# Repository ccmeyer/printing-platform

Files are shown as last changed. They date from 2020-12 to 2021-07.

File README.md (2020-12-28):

# &#181;CD microfluidic printing system
### A system for high throughput reaction generation using sub-microliter droplet printing

<br/>

## Overview

<p align="center">
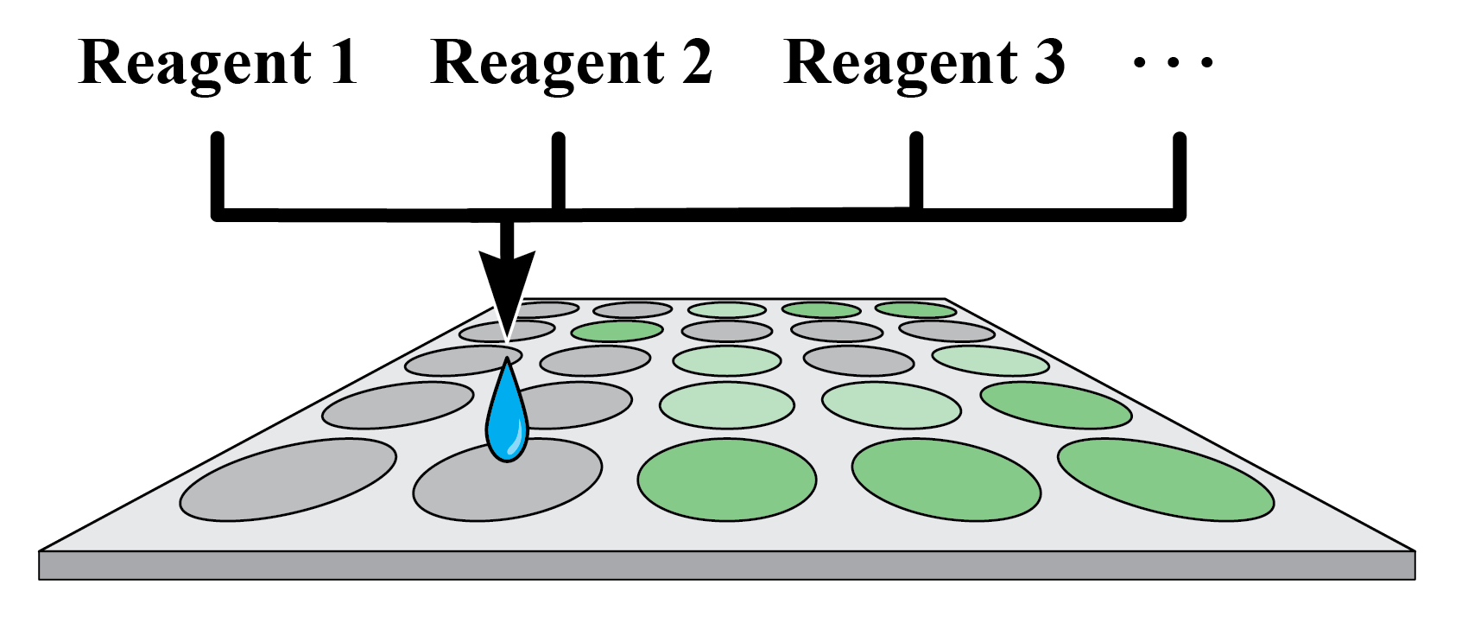
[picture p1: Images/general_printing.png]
  
</p>

The system detailed in this repository was originally described in the paper: "__________" and built upon work described in Wang, J. et al. (2019) Microfluidic cap-to-dispense (μCD): a universal microfluidic–robotic interface for automated pipette-free high-precision liquid handling. Lab Chip 19:3405-3415. This repository includes the necessary components to recreate the system shown in **Figure 1**. This repository includes the following components:
* A parts list, CAD files to 3D print or laser cut the required components, and assembly instructions [link](https://github.com/ccmeyer/printing-platform/blob/main/Documentation/assembly_description.md).

* Description of the underlying theory behind the system and how to optimize its use [link](https://github.com/ccmeyer/printing-platform/blob/main/Documentation/printing_theory_and_calibration.md).

* Description of the API required to control all components of the system [link](https://github.com/ccmeyer/printing-platform/blob/main/Documentation/API_documentation.md).

<br/>

## Printing platform

<p align="center">
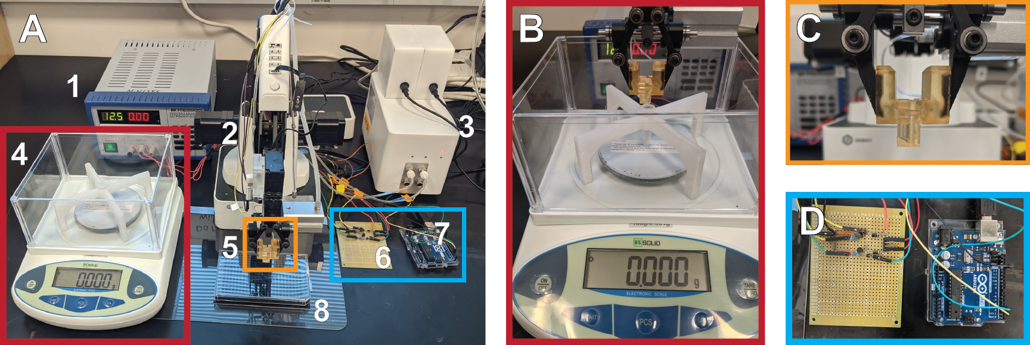
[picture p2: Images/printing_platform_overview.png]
uCD printing system
  
</p>

<p align="center">
  <strong>Figure 1</strong> Diagram of the complete printing platform. (A) Image of the full platform, 1) 12.5V DC power supply, <br>2) Dobot robotic arm, 3) Precigenome pressure regulator, 4) Analytical balance, 5) Gripper holding a printer head, <br>6) Valve control circuit, 7) Arduino Uno microcontroller, 8) Well plate. (B) Close up of the printer head positioned <br>over the reagent tube during calibration. (C) Dobot gripper with the 3D printed gripper adapters holding <br>a printer head. (D) Valve control circuit connected to an Arduino
</p>

The core of the μCD system is a disposable multilayer microfluidic container composed of a 3D printed reservoir linked to a microfluidic printing nozzle with two pneumatic control channels that can be reversibly connected to a robotic arm. This robotic arm is customized to enable reliable linking between the pneumatic controllers and the microfluidic device. The modular and disposable design of the μCD system allows for the inclusion of limitless reagents in a multicomponent experiment as the microfluidic devices are can be swapped in and out without risk of cross-contamination.

The printing platform is comprised of several critical components:
* The three-dimensional positioning and loading of printer heads are achieved using the Dobot magician robotic arm with the gripper attachments. 
* The printing and refuel pressures are regulated by the Precigenome pressure regulator. 
* The Arduino and valves are used to apply the pressures in bursts for printing and refueling.
* The storage and printing is carried out in the disposable microfluidic printing heads.

A detailed description of the components and assembly can be found [here](https://github.com/ccmeyer/printing-platform/blob/main/Documentation/assembly_description.md).

<br/>

## Printing concept

<p align="center">
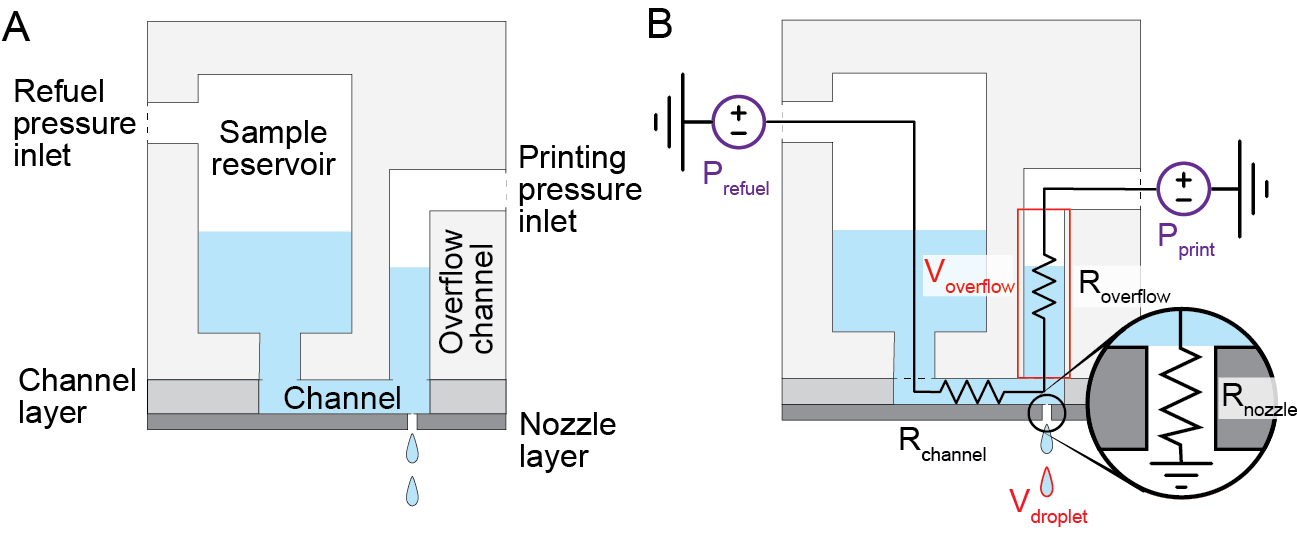
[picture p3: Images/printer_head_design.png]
Printer head design
  
</p>

<p align="center">
  <strong>Figure 2</strong> Schematic depicting the printer head design. A) Labels the components of the printer head. B) Overlay of <br>the parameters of the system. Tunable parameters: purple, fixed parameters: red, unknown parameters: black.
</p>

The system is built upon the concept of microfluidic adaptive printing. The core principle is to apply bursts of force to liquid, squeezing it through a small ejection port (<100 &#181;m) which causes it to pinch off as a nanoliter scale droplet. In our instantiation of this system we use air pressure to exert the force and a small nozzle fabricated out of PMMA to serve as the exit port. The primary variables governing the activity of the system are highlighted in **Figure 2** and are explained in detail [here](https://github.com/ccmeyer/printing-platform/blob/main/Documentation/printing_theory_and_calibration.md).

<br/>

## Platform API

The bulk of the API is included under the umbrella of the `Platform` class. This class includes the functions to intitially connect to and control all of the components that comprise the system. The general tasks that are routinely needed have been divided to make the customization of new protocols accessible. Several manual drive modes have been included to allow for the control of the system from the keyboard. This allows for the quick adaption of processes by the user to prototype protocols or run full experiments. 

The other class is the `PrinterHead` class which is used to track individual printer heads. This makes the tracking of volumes of the reagent are required parameters that are unique to each printer head and reagent to be tracked easily. 

The major steps required to utilize the code is detailed [here](https://github.com/ccmeyer/printing-platform/blob/main/Documentation/API_documentation.md).

<br/>

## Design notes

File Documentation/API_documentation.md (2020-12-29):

# Printing platform API documentation

## `Platform` class

* This is a class used to store the necessary variables required to operate the platform as well as handle all communication with the Dobot, Arduino and pressure regulator

### Dobot communication

`init_dobot()`
* Establishes the connection to the Dobot.
* Sets its movement parameters.
* Reads in the print calibration file which includes the locations of the loading and tube positions.
* Activates the gripper.

`get_plate_data()`
* Reads in the desired file path of the JSON file describing the plate information
* The information includes the well spacing, number of rows and columns and the positions of the four corner wells of the plate
* Generates a transformation matrix to get the corrected well XY-coordinates to ensure accurate Dobot positioning
* Finds the change in Z coordinates moving down the rows or across the columns and assumes a linear change in value to correct the Z coordinate for each well
* To create a new plate use the provided template in the 'Calibrations' directory
* Coordinates are stored as a dictionary with the three keys 'x', 'y', and 'z'

`write_plate_data()`
* Takes all of the current plate data and updates the metadata file that was originally loaded

`gen_trans_matrix()`
* Takes the location of the four corner wells and the plate dimensions and applies the `getPerspectiveTransform()` function from the OpenCV library to perform a four point transformation to map the actual location of the four wells to the expected location
* Then takes the inverse of the matrix so that it can be used to transform the expected coordinates of a well to the actual coordinates

`get_well_coords()`
* Take the desired row and column index and returns the corrected coordinates for the target well
* Uses the transformation matrix to take the expected coordinates and transform them into the real coordinates

`home_dobot()`
* First resets the Dobot's position to avoid having the arm hit the surrounding components during the homing process
* Runs the Dobot homing command
* Sets the location to the 'home' state
* This function should be called before performing any movements with the Dobot to ensure that it has its position correct

`move_dobot()`
* Takes XYZ coordinates and moves the Dobot to those coordinates

`dobot_manual_drive()`
* Drops into a manual drive mode controlled from the keyboard
* X direction is controlled using 'w' and 's'
* Y direction is controlled using 'a' and 'd'
* Z direction is controlled using 'k' and 'm'
* The step or amount that is moved is set using the 'f' to increase the step size and 'v' to decrease it. The step values are in mm
* To quit the manual drive mode, press 'q'

`change_print_position()`
* Initiates a protocol to modify the expected well locations of a given plate
* Moves from corner to corner and drops into `dobot_manual_drive()`to allow the operator to manually drive the Dobot to the correct location of each well to compensate for any deviations
* Once all the points are corrected, the new positions are stored in the plate metadata file.
* It is recommended to run this protocol prior to running any experiments to make sure that the positions are perfect
* Not that necessary for 96-well plates but should always be performed for 384-well plates
* The actual calibration protocol is described in detail [here]

`change_tube_position()`
* Moves to the currently saved tube position used during the printer head calibration protocol
* Drops into the `dobot_manual_drive()` mode to manual correct the position

`move_to_tube_position()`
* Moves to the currently saved tube position used during the printer head calibration protocol
* First moves above the tube to ensure that the arm does not hit the tube as it is located above the plate and the dobot uses point to point movement

`move_to_loading_position()`
* Moves to the currently saved loading position used during the printer head calibration protocol
* Used when switching out printer heads

`move_to_well(row,column)`
* Takes the desired row and column indexes and input and moves to the correct coordinates
* Checks to make sure that the target well is present in the plate

`load_gripper()`
* Initiates a protocol to open and close the gripper to make exchanging printer heads easier.

`disconnect_dobot()`
* Deactivates the gripper
* Disconnects from the Dobot

<br>

### Arduino communication

`init_ard()`
* Takes in the COM port of the Arduino and opens up serial communication
* Currently set to 'COM6' and would need to be changed to the correct COM port if that is incorrect

`print_droplets()`
* Takes the desired frequency, pulse width, refuel width, and droplet count for a printing command
* Serializes all the values and passes it to the Arduino and then pauses briefly
* Sends a second signal to the Arduino to confirm the end of transmission
* Waits to receive a signal from the Arduino that the printing protocol has been completed

`refuel_test()`
* Defined printing protocol used in calibration of the refuel process

`pulse_test()`
* Defined printing protocol used in calibration of the printing step

`refuel_open()`
* Opens the refuel valve and leaves it open

`pulse_open()`
* Opens the printing valve and leaves it open  

`close_valves()`
* Closes both valves

`close_ard()`
* Closes communication with the Arduino

<br>

### Pressure regulator communication

`init_pressure()`
* Initiates the Precigenome pressure regulator and the two channels used for refueling and printing

`set_pressure()`
* Takes in pressure values for the refuel and printing channels

`pressure_on()`
* Turns both pressure channels on

`pressure_off()`
* Turns both pressure channels off

`pressure_test()`
* Used to verify that the complete system is air tight
* Applies high pressure and records the flow
* If the flow rate is high that means that there is a leak in the system that needs to be addressed
* Load the gripper with position calibration chip so that the outlets that connect with the printer heads are seal to ensure proper seal
* The pressure test protocol is described in more detail [here]

`close_reg()`
* Closes communication with the pressure regulator

<br>

### Full platform functions

`initiate_all()`
* Opens communication with all three components

`drive_platform()`
* Comprehensive manually driving function
* Within this method, the operator is able to move the dobot by wells, load and unload the gripper, set and control pressures, and print defined arrays
* The exact functions executed by the drive function can be found in the print_platform_API.py file
* The key assignments can be easily changed to customize the use of drive function

`resistance_testing()`
* Initiates the printer head calibration protocol
* Creates a `PrinterHead` object and asks for the channel volume of the printer being used and then density of the reagent
* Sets the target droplet volume to 60 nL
* Monitors the refuel and printing steps and calculates the resistance of each component of the printer head
* A detailed description of this process can be found [here]

`print_array()`
* Takes a CSV file in the Print_arrays directory and prints the specified number of droplets into the target wells
* A template CSV file can be found in the Print_arrays directory

`disconnect_all()`
* Closes all communication with all three components

<br>

## `PrinterHead` class

* This is a class that is used to store all of the information associated with each printer head required for accurate printing with each printer head.
* Includes specifics about the reagent including its name and density and the printer head such as its overflow channel volume.
* It also contains all of the calibration information including the calculated resistances and the required pressures to print the desired droplet volume. 

<br>

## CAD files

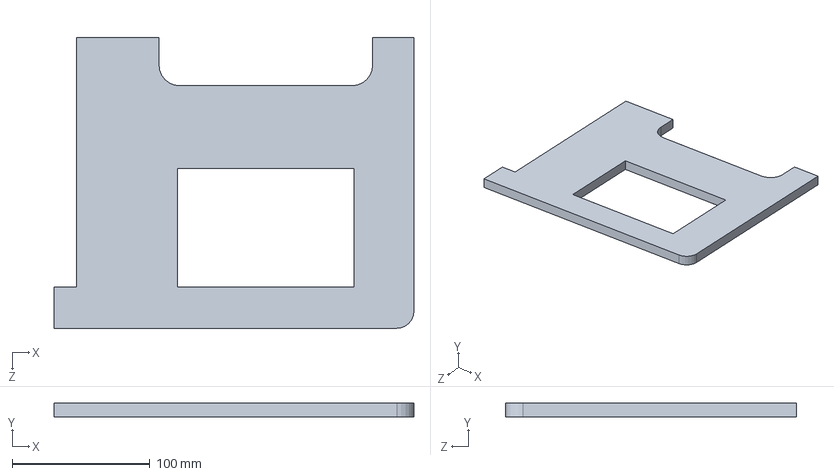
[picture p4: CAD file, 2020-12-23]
CAD_files/arm-plate_holder_template.SLDPRT
261.2 x 10.0 x 210.9 mm

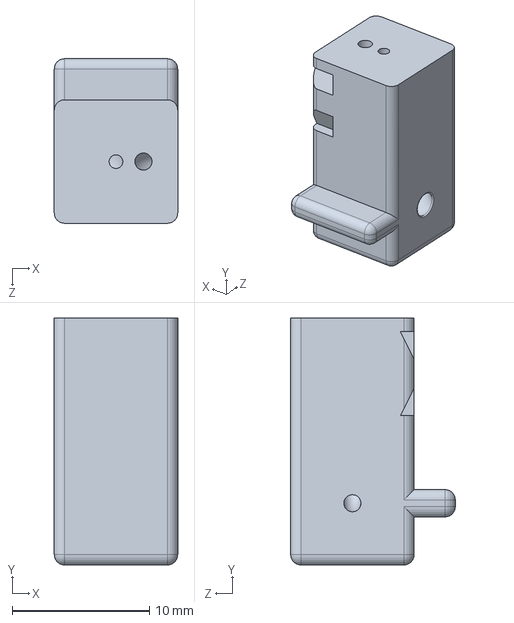
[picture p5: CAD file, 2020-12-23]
CAD_files/printer_head.SLDPRT
9.00 x 18.0 x 12.0 mm

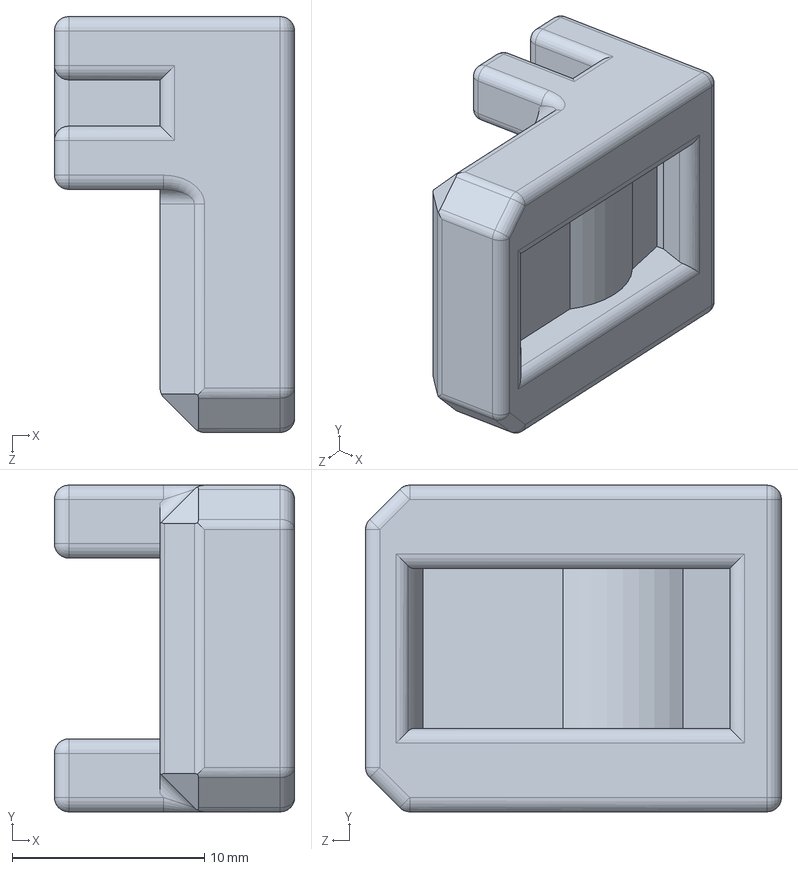
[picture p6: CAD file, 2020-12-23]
CAD_files/gripper_adapter_refuel_side.SLDPRT
12.5 x 17.0 x 21.6 mm

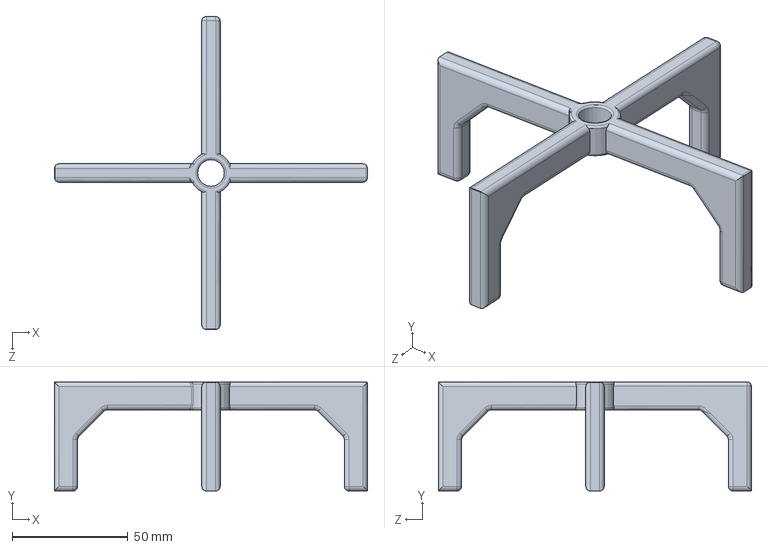
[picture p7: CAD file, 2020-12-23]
CAD_files/balance_tube_holder.SLDPRT
135.0 x 47.0 x 135.0 mm

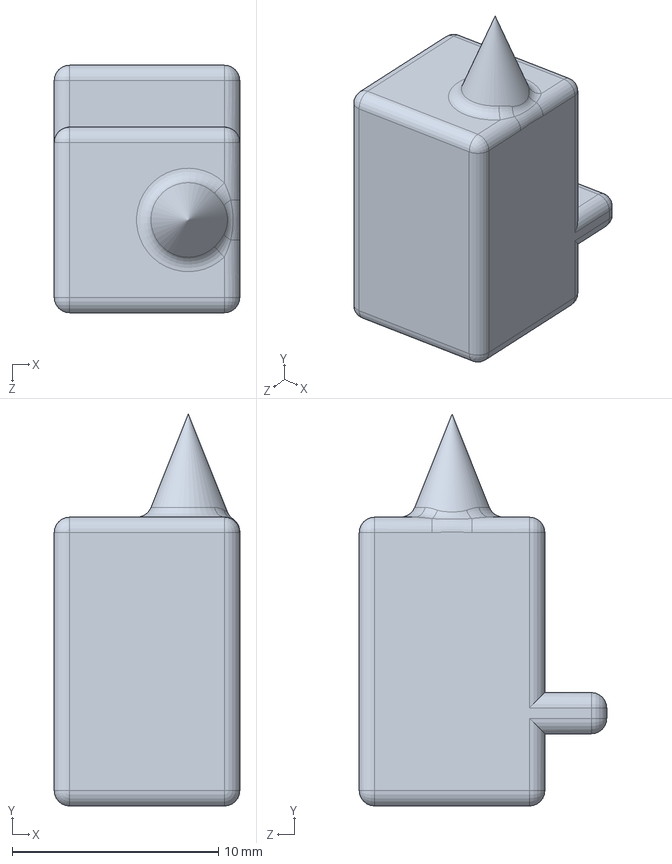
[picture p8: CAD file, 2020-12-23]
CAD_files/position_calibration_chip.SLDPRT
9.00 x 19.0 x 12.0 mm

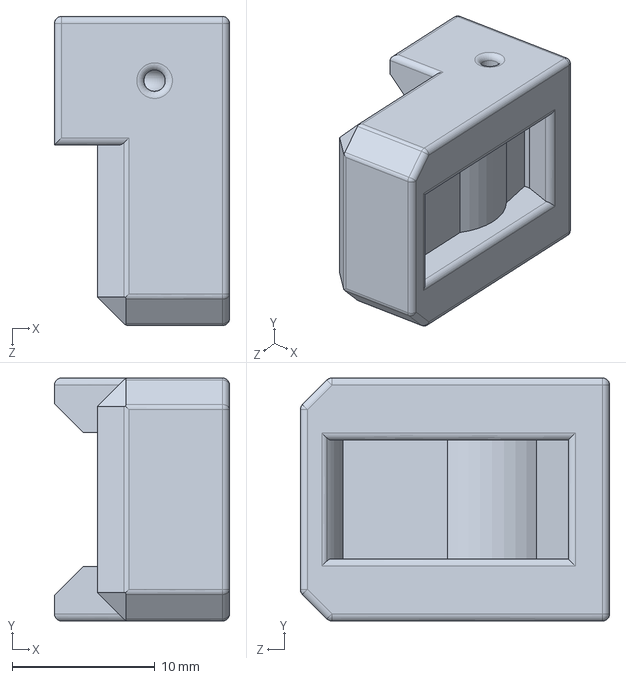
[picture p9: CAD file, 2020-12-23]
CAD_files/gripper_adapter_print_side.SLDPRT
12.2 x 17.0 x 21.6 mm

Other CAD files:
CAD_files/balance_tube_holder.STL
CAD_files/gripper_adapter_print_side.STL
CAD_files/gripper_adapter_refuel_side.STL
CAD_files/position_calibration_chip.STL
CAD_files/printer_head.STL

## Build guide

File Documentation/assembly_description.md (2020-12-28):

# Printing platform assembly

<p align="center">
  µCD printing system
</p>

<p align="center">
  <strong>Figure 1</strong> Diagram of the complete printing platform. (A) Image of the full platform, 1) 12.5V DC power supply, <br>2) Dobot robotic arm, 3) Precigenome pressure regulator, 4) Analytical balance, 5) Gripper holding a printer head, <br>6) Valve control circuit, 7) Arduino Uno microcontroller, 8) Well plate. (B) Close up of the printer head positioned <br>over the reagent tube during calibration. (C) Dobot gripper with the 3D printed gripper adapters holding <br>a printer head. (D) Valve control circuit connected to an Arduino
</p>

The printing platform is comprised of several different components. The three-dimensional positioning and loading of printer heads are achieved using the Dobot magician robotic arm with the gripper attachments. The printing and refuel pressures are regulated by the Precigenome pressure regulator. The Arduino and valves are used to apply the pressures in bursts for printing and refueling. The assembled system is shown in **Figure 1**. 

## Material list

1.	PMMA sheets (75 μm thick)
2.	Double-sided adhesive membrane (ARcare 90445, Adhesives Research, 80 μm thick)
3.	CO2 laser cutter (Universal Laser Systems, VersaLaser 2.30)
4.	85 μm nozzle in 75 μm thick PMMA (Jestar Mold Tech Co., Ltd)
5.	SLA 3D printer (Form 3 Formlabs)
6.	Clear Resin (Formlabs)
7.	Analytical Balance (U.S Solid 1mg or ideally 0.1mg precision)
8.	Robotic arm (Dobot Magician)
9.	Two mini solenoid valves (LHDA1221111H, Lee Co)
10.	Manifold (Lee Co.)
11.	Automated pressure regulator (Precigenome Pressure/Flow controller light version, PG-MFC-LT2CH-X)
12.	Microcontroller (Arduino Uno)
13.	12.5V Power supply (BK precision programmable DC power supply)
14.	Thin tubing (1/16” and 1/8” Tygon® S3™ E-3603 Non-DEHP Laboratory Tubing)
15	Diode 1N4005
16.	Zener Diode 1N4757 51V
17.	Transistor MJH11022G
18.	Resistor 330 Ω
19.	Connector wires
20.	Breadboard

## Steps to assembe the platform

1. Connect the gripper attachment to the Dobot 

2. 3D print the two different gripper adapters for both the refuel and printing side. Attach the gripper adapters, shown in **Figure 2**, to the end effector.

<p align="center">
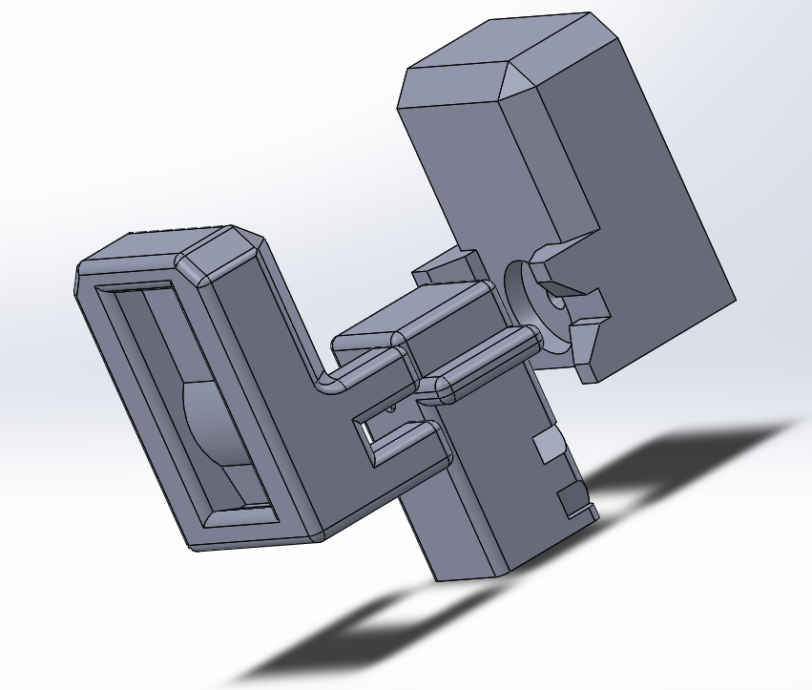
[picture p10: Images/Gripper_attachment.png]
Gripper attachments
  
</p>

<p align="center">
  <strong>Figure 2</strong> Gripper adapters used to accurately grip the printer heads
</p>

2. Screw each valve into the manifold and attach it to Dobot near the gripper (see Note 11).

3. Connect the gripper adapters to the manifolds using the thin tubing. Then connect the manifolds to the corresponding pressure outlets on the Precigenome pressure regulator.

4. Construct the circuit shown in **Figure 3** and connect the Arduino, the two valves and the power source to it Provide enough extra tubing and wires to run them along the arm to not restrict its motion while in use.

<p align="center">
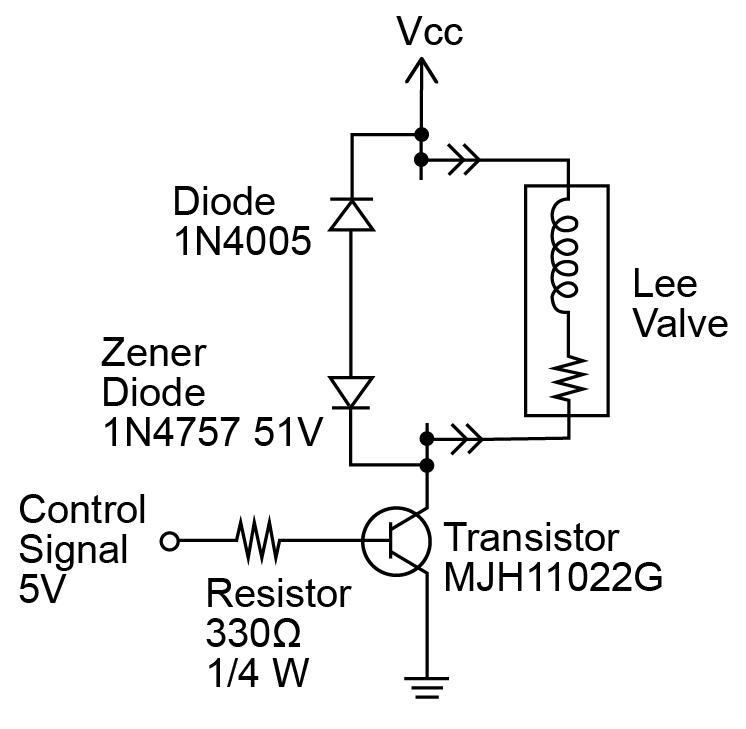
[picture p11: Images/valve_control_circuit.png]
Valve control circuit
  
</p>

<p align="center">
  <strong>Figure 3</strong> Circuit design used to regulate the valves controlling the pressure flow using the Arduino
</p>

5.	Set the voltage of the power source to 12.0 V or the required voltage for the valves.

6.	Laser cut the provided [template] and place around the Dobot to provide consistent placement of the well plate and balance in the Dobot’s Cartesian coordinate system.

7.	Connect the arm, the pressure regulator, and the Arduino to your computer.

8.	Upload the provided Arduino program to the Arduino provided [here].

9.	3D print the tube stand and place on top of the scale.

## Steps to assemble the printer heads

1.	To fabricate the layer with the small nozzle, a UV-laser is used to ablate a small hole (65-85µm diameter) into a PMMA sheet. A range of nozzle diameters can be used to give different size droplets. The nozzles can be fabricated by the following companies: Jestar Mold Tech Co., Ltd (China) and Micron Laser Technology Inc. (USA).

2.	The channel layer can be fabricated using a CO2 laser to ablate microchannels in double-sided membrane adhesive. The chosen channel width was 200 μm.	A wide range of channel widths and lengths can be used. Choose the width based on the desired channel resistance. 

3.	The bulk component of the printer head, which contains the connections to the pressure inlets and the reagent reservoir, is fabricated by 3D printing. We used stereolithography (SLA) printing with surgical guide photosensitive resin to generate the printer heads and the gripper adapters. It is critical that these printer heads are watertight, transparent and have smooth channels for proper use. These qualities are very difficult to achieve with standard fused deposition modeling (FDM) printers as there are many imperfections at the junctions between layers.

4.	The full printer head is assembled stepwise:

5.	Peel one side from the adhesive layer containing the channel and adhere it to the bottom of the 3D printed component. Line up the entry and exit holes of the channel with the corresponding openings on the 3D printed part.

6.  Peel off the other side of the adhesive layer and place the nozzle layer on top. Ensure that the small nozzle is lined up with the exit of the channel. Firmly press the layers down to make sure that there are no air pockets.

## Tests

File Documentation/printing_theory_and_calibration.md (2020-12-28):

# Printing theory

<p align="center">
  Printer head design
</p>

<p align="center">
  <strong>Figure 1</strong> Schematic depicting the printer head design. A) Labels the components of the printer head. B) Overlay of the parameters of the system. Tunable parameters: purple, fixed parameters: red, unknown parameters: black.
</p>

The complicated underlying fluid dynamics of the droplet printing system can be modeled using a simple fluid flow equation relating pressure, flow, and resistance.

<p align="center">
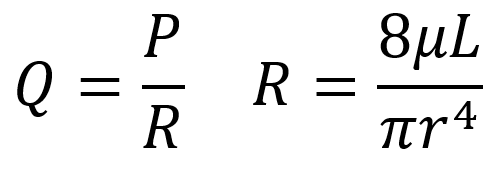
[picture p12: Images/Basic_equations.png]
Basic equations
  
</p>

In the above equations Q is flow, P is pressure, R is resistance, &#181; is viscoity, L is length, and r is the radius of the channel. At the scale of this system the interfacial tension and surface roughness and other unknown factors cause the resistance to not follow this idealized description. However, this equation helps depict the variables that the resistance, and therefore flow, depends on. Specifically the viscosity of the reagent and the radius of the nozzle. The major variables of this system are shown in **Figure 1** using the same notation as above.

While in an ideal world the properties of all reagents would be the same and the fabrication would be perfect, in reality these are often not true. The viscosity of different reagents can vary starkly such as comparing cell lysate to water. The fabrication, especially of the small nozzle, often varies and when the resistance of the nozzle is dependent on the radius of the hole to the fourth power small imperfections lead to deviations from the expected droplet volume. 

To address this issue, a calibration method has been developed to rapidly account for the differences in the printer head and the reagent simultaneouslly to achieve nanoliter resolution.

<br>

# Calibration theory

The fundamental idea of this calibration process is to leverage the fixed and tunable parameters to both determine and then account for the unknown parameters. The parameters of the system are: Unknown - Channel and nozzle resistances; Fixed - Overflow chamber volume; Tunable - Refuel and printing pressures. The primary objective of this process is to determine the printing pressure needed to eject the desired droplet volume and the refueling pressure to replenish the overflow chamber for continuous printing.

The pressures can be determined using a simple stepwise procedure beginning by calculating the unknown channel, total, and nozzle resistances

### Refuel resistance

<p align="center">
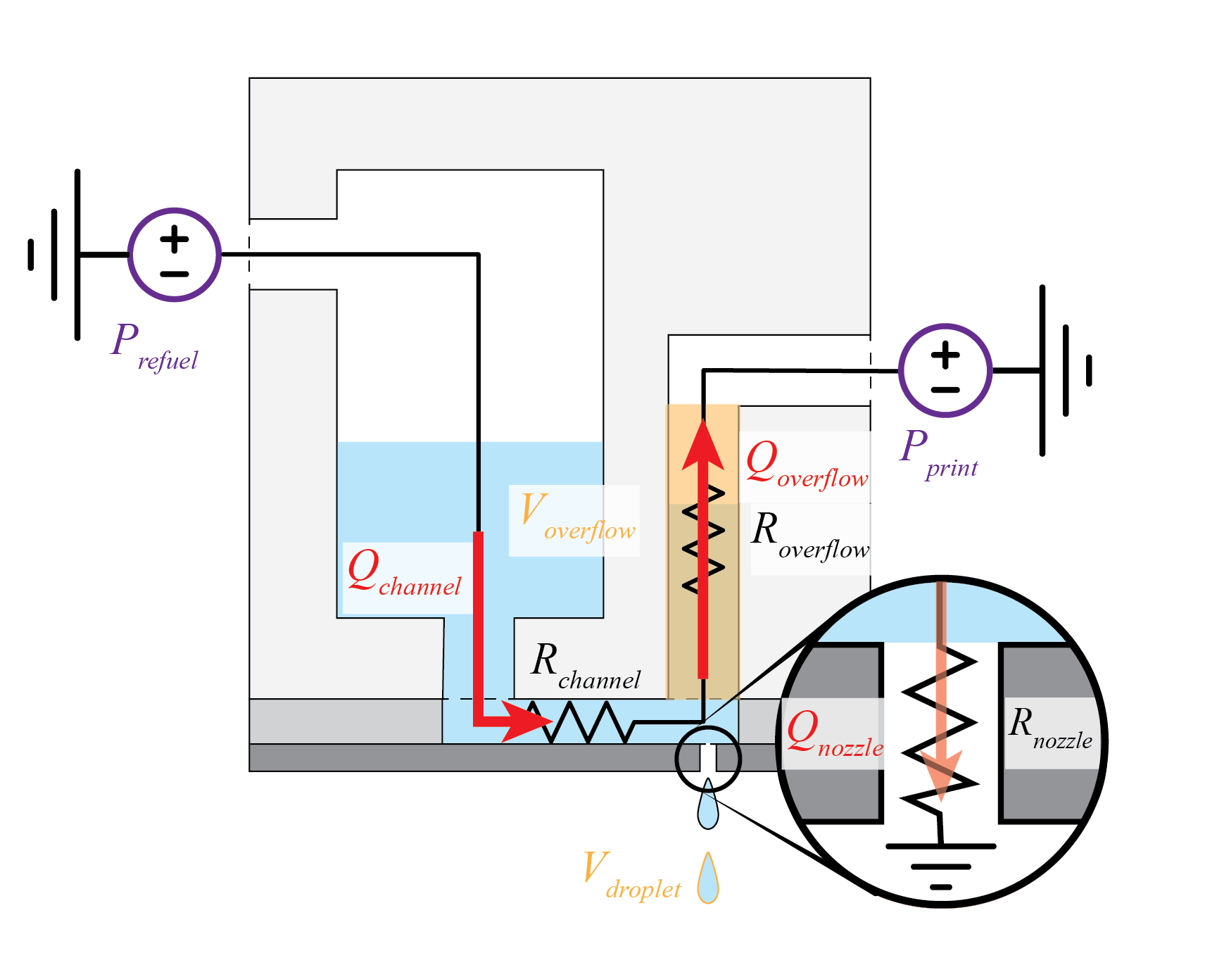
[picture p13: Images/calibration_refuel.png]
Refuel
  
</p>

<p align="center">
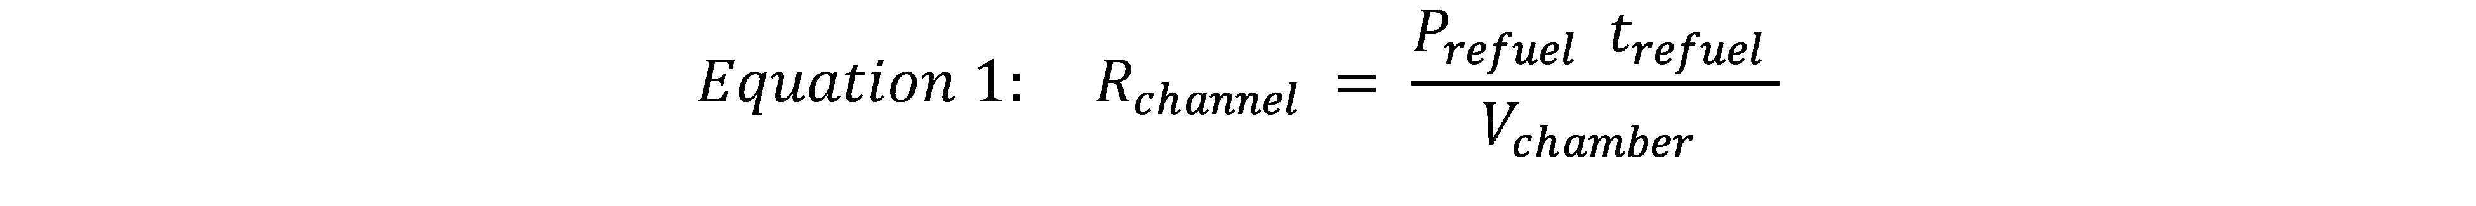
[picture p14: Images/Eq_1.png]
Equation 1
  
</p>

By applying small bursts of refuel pressure, the time required to fill the volume of the overflow channel using a set pressure can be determined. Plugging these values into Equation 1 gives the resistance of the channel. 

<br>

### Total printing resistance

<p align="center">
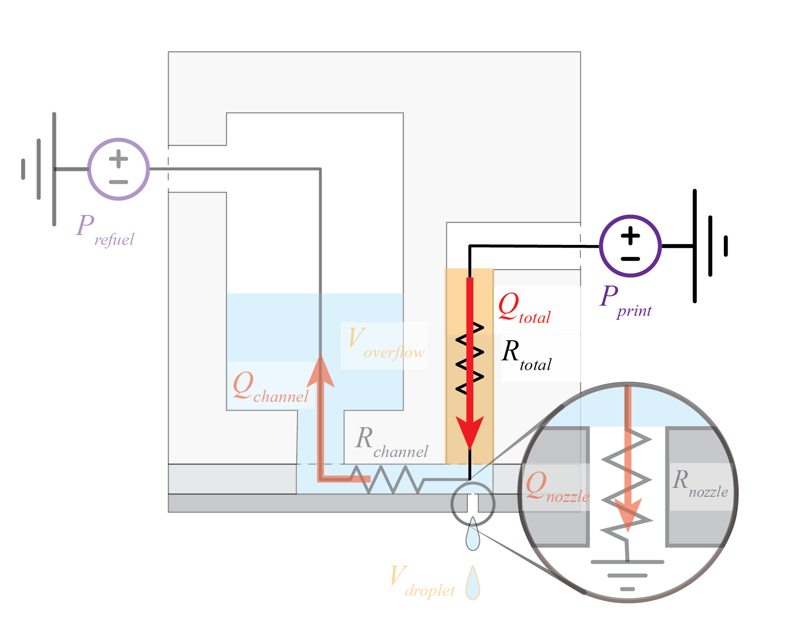
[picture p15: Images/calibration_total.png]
Total
  
</p>

<p align="center">
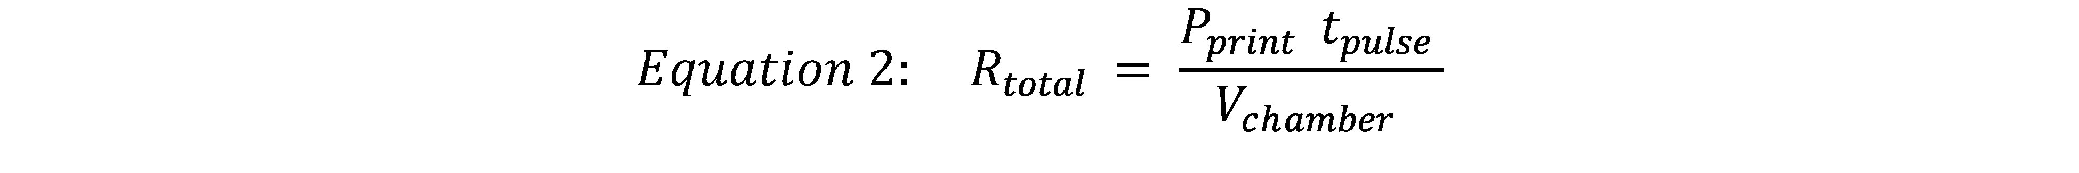
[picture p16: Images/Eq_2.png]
Equation 2
  
</p>

The total printing resistance is calculated using the same process as was used to find the refuel resistance except that now the printing pressure is applied in bursts and the time required to empty the overflow channel is monitored. Using Equation 2 allows for the calculation of the total printing resistance. This resistance does not represent the resistance of the nozzle as the flow out of the overflow channel is split between flowing through the nozzle and back through the channel. This value is necessary to know for later tuning the refuel pressure. By changing the channel length and width will change the resistance of the channel which will modulate how much back flow there is.

<br>

### Nozzle resistance
<p align="center">
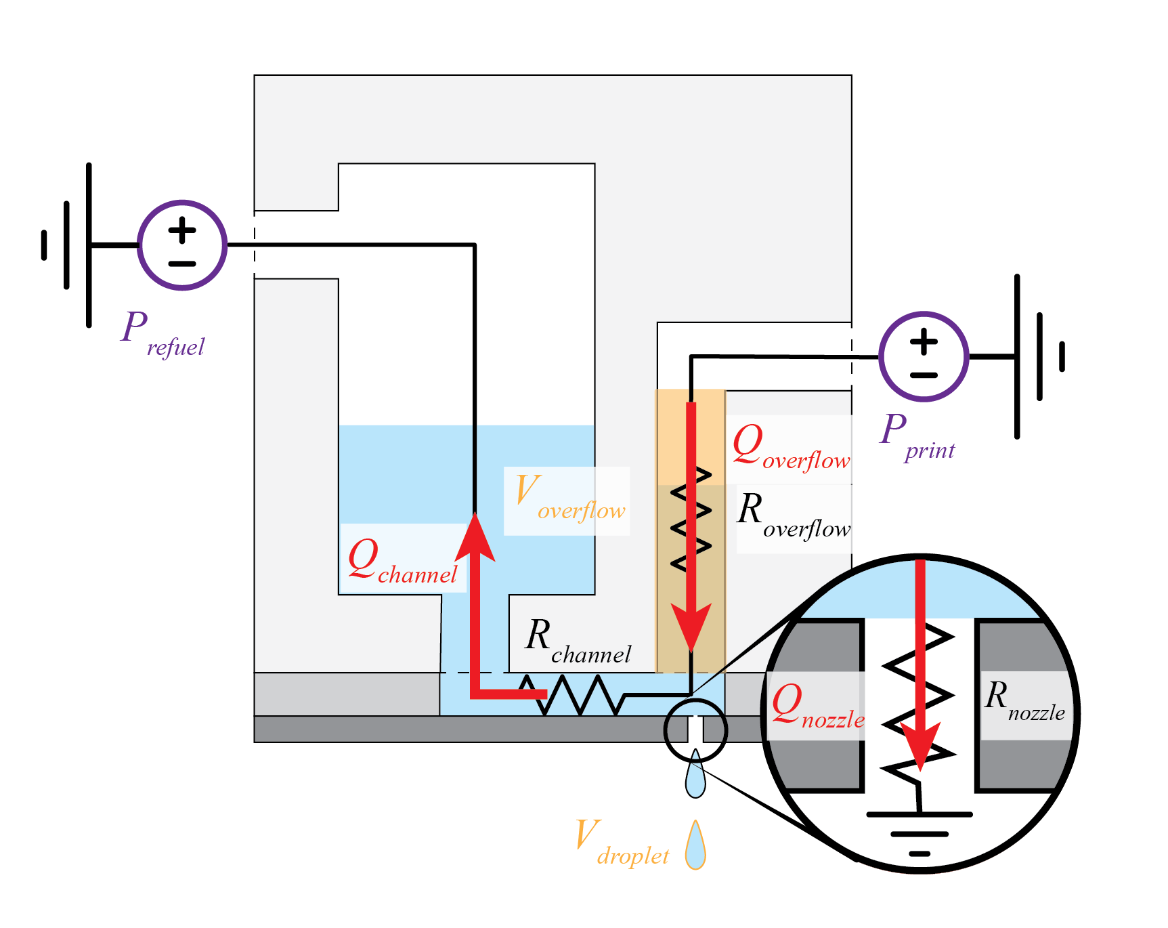
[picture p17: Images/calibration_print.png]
Print
  
</p>

<p align="center">
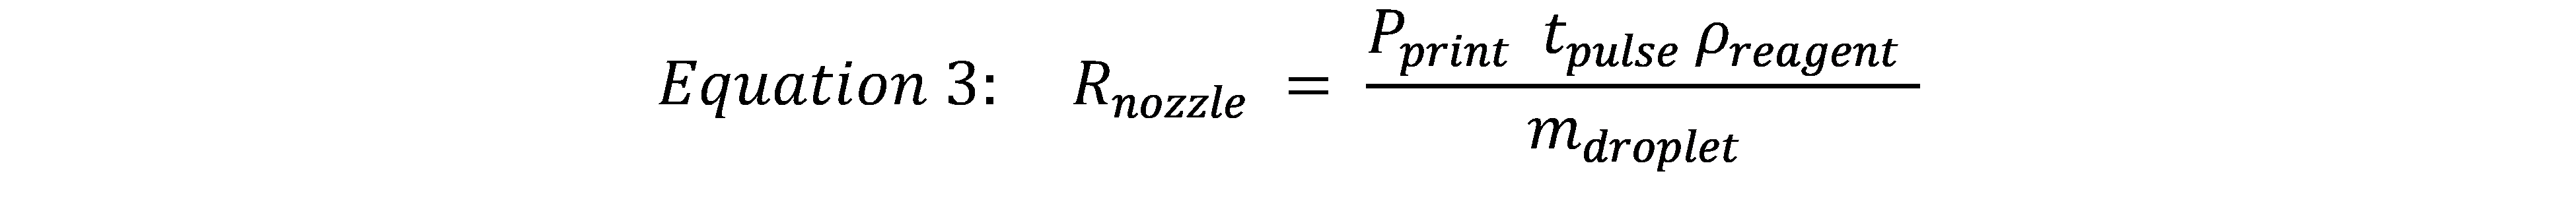
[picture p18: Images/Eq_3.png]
Equation 3
  
</p>

Through the process of calculating the total resistance, the ejected droplets are collected and used to calculate the volume of liquid that was displaced during the printing bursts. Using this volume and the known pressure and time of its application, the flow through the nozzle and its resistance can be calculated using Equation 3.

<br>

### Printing pressure 

<p align="center">
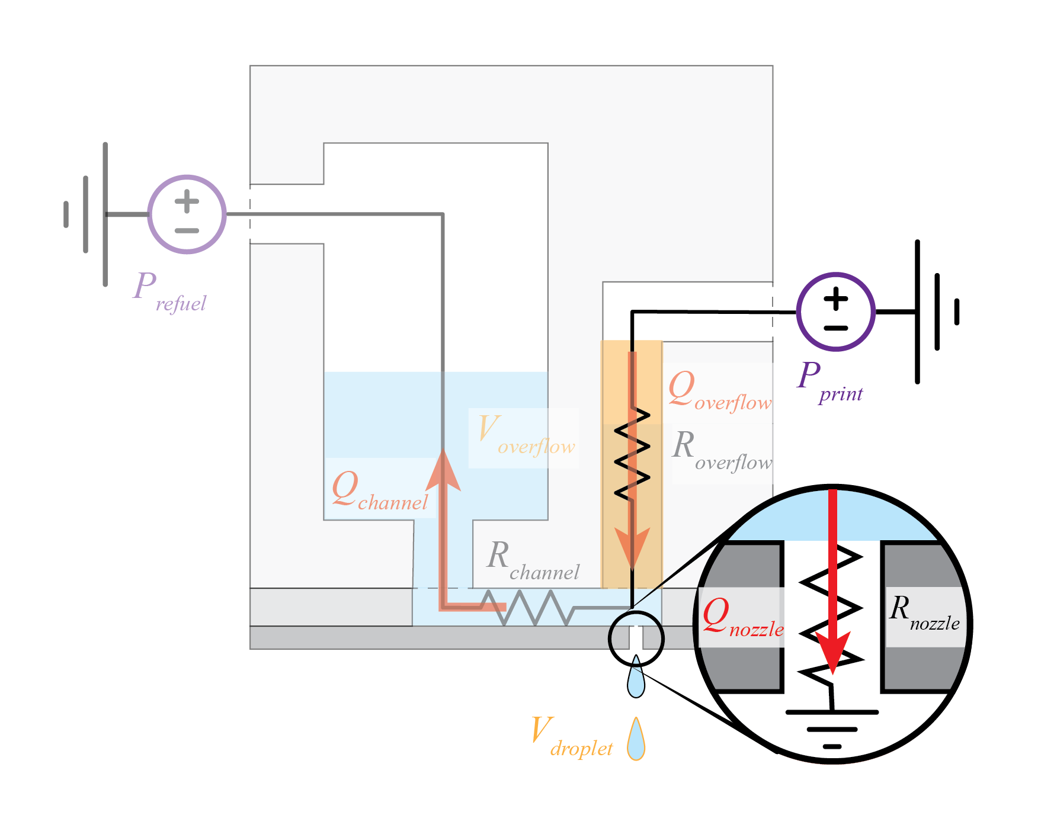
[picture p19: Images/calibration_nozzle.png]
Nozzle
  
</p>

<p align="center">
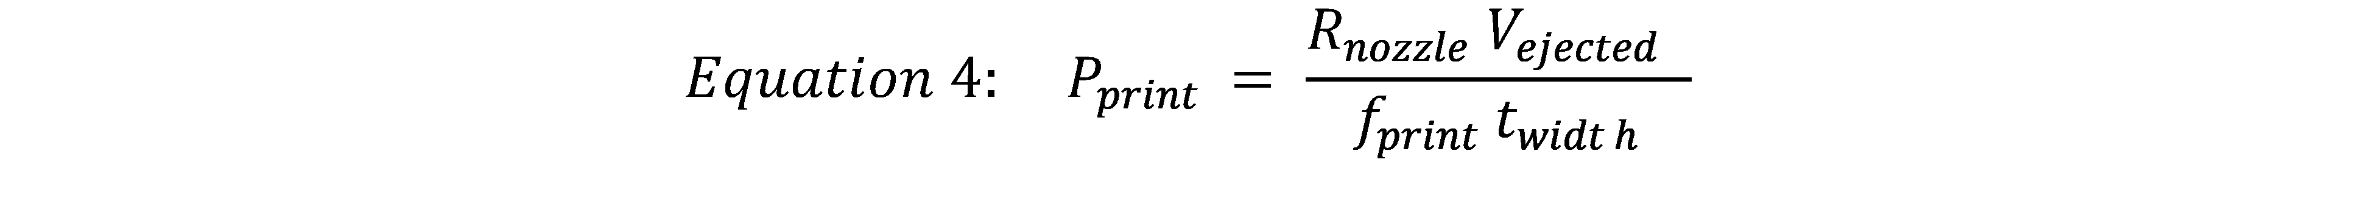
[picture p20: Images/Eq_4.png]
Equation 4
  
</p>

With the calculated nozzle resistance, the required printing pressure can be calculated to print the desired droplet volume using Equation 4.

<br>

### Refuel pressure

<p align="center">
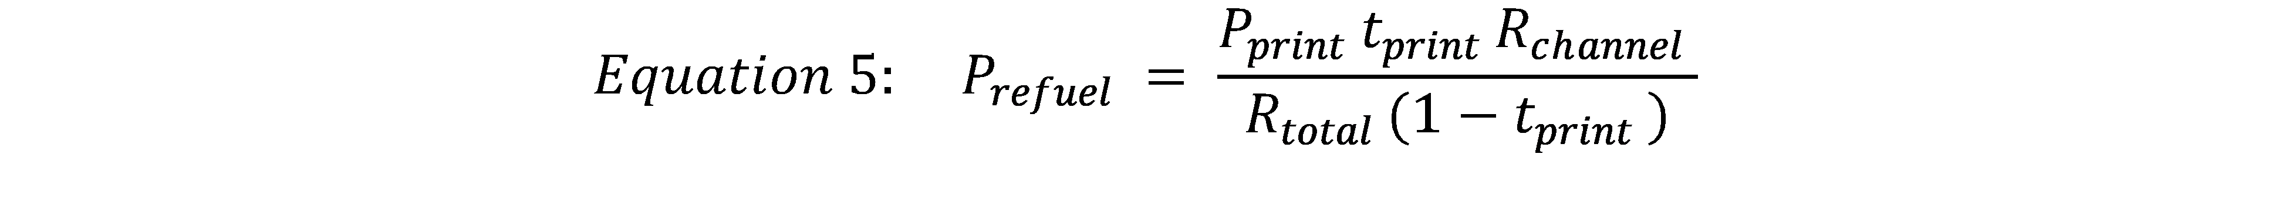
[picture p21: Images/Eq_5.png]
Equation 5
  
</p>

Once the printing pressure is determined, the refuel pressure can be set to account for the displaced volume during printing. Using the calculated refuel and total printing resistances in Equation 5 allows for the calculation of the necessary refuel pressure. In Equation 5, f represents the frequency of printing and t represents the duration of each printing pulse. To maximize the activity of the system we have set the refuel pressure to be active whenever the printing pressure is not applied. It is recommended to keep these parameters constant and only adjust the pressures as there are unknown changes in the resistance due to changes in those parameters. We use a pulse width of 3 msec and a frequency of 20 Hz. 

<br>

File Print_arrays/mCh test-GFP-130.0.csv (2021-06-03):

Row | Column | Droplet
0 | 1 | 4
0 | 8 | 4
0 | 10 | 4
0 | 13 | 4
0 | 21 | 4
0 | 22 | 4
1 | 0 | 4
1 | 3 | 4
1 | 4 | 4
1 | 10 | 4
1 | 15 | 4
1 | 16 | 4
2 | 0 | 4
2 | 2 | 4
2 | 4 | 4
2 | 7 | 4
2 | 17 | 4
3 | 3 | 4
3 | 16 | 4
3 | 17 | 4
4 | 3 | 4

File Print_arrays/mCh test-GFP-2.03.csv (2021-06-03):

Row | Column | Droplet
0 | 7 | 2
0 | 12 | 2
0 | 14 | 2
0 | 17 | 2
0 | 18 | 2
1 | 7 | 2
1 | 19 | 2
1 | 21 | 2
1 | 23 | 2
2 | 5 | 2
2 | 11 | 2
2 | 22 | 2
2 | 23 | 2
3 | 2 | 2
3 | 6 | 2
3 | 7 | 2
3 | 10 | 2
3 | 21 | 2
3 | 23 | 2
4 | 2 | 2
4 | 6 | 2

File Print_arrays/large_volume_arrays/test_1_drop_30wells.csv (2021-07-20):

Row | Column | Droplet
0 | 0 | 1
0 | 1 | 1
0 | 2 | 1
0 | 3 | 1
0 | 4 | 1
0 | 5 | 1
0 | 6 | 1
0 | 7 | 1
0 | 8 | 1
0 | 9 | 1
0 | 10 | 1
0 | 11 | 1
0 | 12 | 1
0 | 13 | 1
0 | 14 | 1
0 | 15 | 1
0 | 16 | 1
0 | 17 | 1
0 | 18 | 1
0 | 19 | 1
0 | 20 | 1
0 | 21 | 1
0 | 22 | 1
0 | 23 | 1
1 | 23 | 1
1 | 22 | 1
1 | 21 | 1
1 | 20 | 1
1 | 19 | 1
1 | 18 | 1
1 | 17 | 1
1 | 16 | 1
1 | 15 | 1
1 | 14 | 1
1 | 13 | 1
1 | 12 | 1
1 | 11 | 1
1 | 10 | 1
1 | 9 | 1
1 | 8 | 1
1 | 7 | 1
1 | 6 | 1
1 | 5 | 1
1 | 4 | 1
1 | 3 | 1
1 | 2 | 1
1 | 1 | 1
1 | 0 | 1
2 | 0 | 1
2 | 1 | 1
2 | 2 | 1
2 | 3 | 1
2 | 4 | 1
2 | 5 | 1
2 | 6 | 1
2 | 7 | 1
2 | 8 | 1
2 | 9 | 1
2 | 10 | 1
2 | 11 | 1
2 | 12 | 1
2 | 13 | 1
2 | 14 | 1
2 | 15 | 1
2 | 16 | 1
2 | 17 | 1
2 | 18 | 1
2 | 19 | 1
2 | 20 | 1
2 | 21 | 1
2 | 22 | 1
2 | 23 | 1
3 | 23 | 1
3 | 22 | 1
3 | 21 | 1
3 | 20 | 1
3 | 19 | 1
3 | 18 | 1
3 | 17 | 1
3 | 16 | 1
3 | 15 | 1
3 | 14 | 1
3 | 13 | 1
3 | 12 | 1
3 | 11 | 1
3 | 10 | 1
3 | 9 | 1
3 | 8 | 1
3 | 7 | 1
3 | 6 | 1
3 | 5 | 1
3 | 4 | 1
3 | 3 | 1
3 | 2 | 1
3 | 1 | 1
3 | 0 | 1

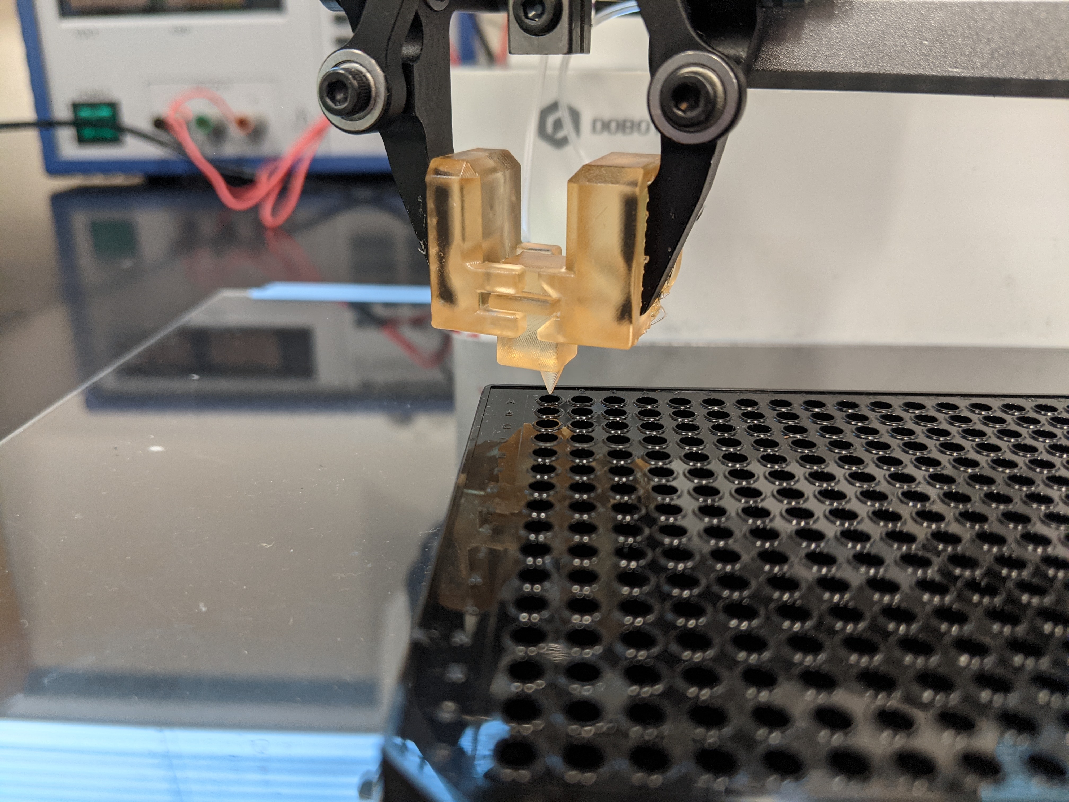
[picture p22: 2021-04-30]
Images/position_calibration.jpg

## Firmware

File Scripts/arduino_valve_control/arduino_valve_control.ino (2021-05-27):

#include <Wire.h>
// int data[7]; // seven bytes sent to Arduino each time
//  int count = 0;
//  int start = 0;

const int valveP = 2;  // for Pulse
const int valveR = 3;  // for Refill

byte datard[16] = {0, 0, 0, 0, 0, 0, 0, 0, 0, 0, 0, 0, 0, 0, 0, 0};
int PW;
int Freq;
int RePW;
int pulsecount;
int pulseswitch = 0;
int DeTi = 50;

int i = 0;
int j = 0;
int lim = 0;
int tp = 0;
byte inByte = 0;

void ParamPass()     // receive cmd data after flush the buffer, while stopping output pulse
{

  if (Serial.available()) {
    for (i = 0; i < 16; i++){
      datard[i] = 0;
    }
    i = 0;
    while (Serial.available()){
      inByte = Serial.read();
//      Serial.write(inByte);
      if (i < 12){
        datard[i] = inByte;
        i++;
      }
      else {
        while (Serial.available()){
          inByte = Serial.read();
        }
        break;
      }
    }
    i = 0;
    while (i <= 8){
      if (datard[i] == 255 && datard[i + 1] == 255) {
        if (datard[i + 2] == 254 && datard[i + 3] == 254) {   // FE FE
          pulseswitch = 0;
          i=i+4;
          //break;
        } else if (datard[i + 2] == 239 && datard[i + 3] == 239) {   // EF EF
          pulseswitch = 1;
          //break;
          i=i+4;
        } else if (datard[i + 2] == 237 && datard[i + 3] == 237) {   // EF EF
          pulseswitch = 2;
          //break;
          i=i+4;
        } else if (datard[i + 2] == 235 && datard[i + 3] == 235) {   // EF EF
          pulseswitch = 3;
          //break;
          i=i+4;
        }
        else {
          Freq = datard[i + 2];
          tp = 1000 / Freq;
          PW = datard[i + 4] * 256 + datard[i + 3];
          RePW = datard[i + 6] * 256 + datard[i + 5];
          pulsecount = datard[i + 7];
          i=i+8;
          //break;
        }
      } else {
        i++;
      }
    }
  }
}



void setup() { // put your setup code here, to run once:
  Serial.begin(115200);
  Serial.setTimeout(100);
//  Serial.write('R');
  while (!Serial) {
  ;   // wait for serial port to connect. Needed for Leonardo only
  }
    pinMode(2, OUTPUT);
    pinMode(3, OUTPUT);
    pinMode(4, OUTPUT);
    pinMode(5, OUTPUT);
    pinMode(6, OUTPUT);
    pinMode(7, OUTPUT);
    pinMode(8, OUTPUT);
    pinMode(9, OUTPUT);
    pinMode(10, OUTPUT);
    pinMode(11, OUTPUT);
    pinMode(12, OUTPUT);
    pinMode(13, OUTPUT);
    digitalWrite(2, LOW);
    digitalWrite(3, LOW);
    digitalWrite(4, LOW);
    digitalWrite(5, LOW);
    digitalWrite(6, LOW);
    digitalWrite(7, LOW);
    digitalWrite(8, LOW);
    digitalWrite(9, LOW);
    digitalWrite(10, LOW);
    digitalWrite(11, LOW);
    digitalWrite(12, LOW);
    digitalWrite(13, LOW);
  }

void loop() {
  ParamPass();
  if (pulseswitch == 1) {
    if(PW == 0){    // Refuel test
      for(j=0; j < pulsecount; j++){
        delay(1000/Freq/2 - RePW/1000/2);
        digitalWrite(valveR, HIGH);
        delayMicroseconds(RePW);
        digitalWrite(valveR, LOW);
        delay(1000/Freq/2 - RePW/1000/2);
      }
    }
    else if(RePW == 0){   //Pulse test
      for(j=0; j < pulsecount; j++){
        delay(1000/Freq/2 - PW/1000/2);
        digitalWrite(valveP, HIGH);
        delayMicroseconds(PW);
        digitalWrite(valveP, LOW);
        delay(1000/Freq/2 - PW/1000/2);
      }
    }

    else {    //Normal droplet printing with refuel open when not pulsing
      for(j=0; j < pulsecount; j++){
        delay(1000/Freq/2 - PW/1000/2);
        digitalWrite(valveR, LOW);
        digitalWrite(valveP, HIGH);
        delayMicroseconds(PW);
        digitalWrite(valveP, LOW);
        digitalWrite(valveR, HIGH);
        delay(1000/Freq/2 - PW/1000/2);
      }
    }
    digitalWrite(valveP, LOW);
    digitalWrite(valveR, LOW);
    pulseswitch = 0;
    delay(100);
    Serial.write('C');
    if (pulsecount == 0){
      Serial.write('N');
    }
    if (Freq == 0){
      Serial.write('F');
    }
    //delay(100);
    //Serial.write('C');
    //delay(100);
    //Serial.write('E');

  } else if (pulseswitch == 2) {
//    digitalWrite(valveP, LOW);
    Serial.write('R');
    digitalWrite(valveR, HIGH);
    delay(100);
  } else if (pulseswitch == 3) {
    Serial.write('P');
    digitalWrite(valveP, HIGH);
//    digitalWrite(valveR, LOW);
    delay(100);
  } else {
    Serial.write('E');
    digitalWrite(valveP, LOW);
    digitalWrite(valveR, LOW);
    delay(100);
  }
}

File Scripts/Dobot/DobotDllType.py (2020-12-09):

from ctypes import *
import time,  platform
import os

def enum(**enums):
    return type("Enum", (), enums)

EndType = enum(EndTypeCustom=0,
    EndTypeSuctionCup=1,
    EndTypeGripper=2,
    EndTypeLaser=3,
    EndTypePen = 4,
    EndTypeMax=5)

DevType = enum(Idle=0,
               Conntroller=1,
               Magician=2,
               MagicianLite=3
               )

ParamsMode = enum(JOG=0,
                other=1)



class DevInfo(Structure):
    _pack_ = 1
    _fields_ = [
        ("devId", c_int),
        ("type", c_int),
        ("firmwareName", c_byte * 50),
        ("firwareVersion", c_byte * 50),
        ("runTime", c_float)
               ]

class ConnectInfo(Structure):
    _pack_ = 1
    _fields_ = [
        ("masterDevInfo", DevInfo),
        ("slaveDevInfo1", DevInfo),
        ("slaveDevInfo2", DevInfo)
    ]

class UpgradeFWReadyCmd(Structure):
    _pack_ = 1
    _fields_ = [
        ("fwSize", c_uint32),
        ("md5", c_char_p)
    ]

class DeviceID(Structure):
    _pack_ = 1
    _fields_ = [
        ("deviceID1", c_uint32),
        ("deviceID2", c_uint32),
        ("deviceID3", c_uint32)
    ]

masterId = 0
slaveId = 0

class DeviceVersion(Structure):
    _pack_ = 1
    _fields_ = [
        ("fw_majorVersion", c_byte),
        ("fw_minorVersion", c_byte),
        ("fw_revision", c_byte),
        ("fw_alphaVersion", c_byte),
        ("hw_majorVersion", c_byte),
        ("hw_minorVersion", c_byte),
        ("hw_revision", c_byte),
        ("hw_alphaVersion", c_byte)
    ]

# For EndTypeParams
class EndTypeParams(Structure):
    _pack_ = 1
    _fields_ = [
        ("xBias", c_float),
        ("yBias", c_float),
        ("zBias", c_float)
        ]

class Pose(Structure):
    _pack_ = 1
    _fields_ = [
        ("x", c_float),
        ("y", c_float),
        ("z", c_float),
        ("rHead", c_float),
        ("joint1Angle", c_float),
        ("joint2Angle", c_float),
        ("joint3Angle", c_float),
        ("joint4Angle", c_float)
        ]

class Kinematics(Structure):
    _pack_ = 1
    _fields_ = [
        ("velocity", c_float),
        ("acceleration", c_float)
        ]

class AlarmsState(Structure):
    _pack_ = 1
    _fields_ = [
        ("alarmsState", c_int32)
        ]

class HOMEParams(Structure):
    _pack_ = 1
    _fields_ = [
        ("x", c_float),
        ("y", c_float),
        ("z", c_float),
        ("r", c_float)
        ]

class HOMECmd(Structure):
    _pack_ = 1
    _fields_ = [
        ("temp", c_float)
        ]

class AutoLevelingCmd(Structure):
    _pack_ = 1
    _fields_ = [
        ("controlFlag", c_ubyte),
        ("precision", c_float)
        ]

class EMotor(Structure):
    _pack_ = 1
    _fields_ = [
        ("index", c_byte),
        ("isEnabled", c_byte),
        ("speed", c_int32)
        ]

class EMotorS(Structure):
    _pack_ = 1
    _fields_ = [
        ("index", c_byte),
        ("isEnabled", c_byte),
        ("speed", c_int32),
        ("distance", c_uint32)
        ]

##################  Arm orientation定义   ##################
ArmOrientation = enum(
    LeftyArmOrientation=0,
    RightyArmOrientation=1)

##################  点动示教部分   ##################

class JOGJointParams(Structure):
    _pack_ = 1
    _fields_ = [
        ("joint1Velocity", c_float),
        ("joint2Velocity", c_float),
        ("joint3Velocity", c_float),
        ("joint4Velocity", c_float),
        ("joint1Acceleration", c_float),
        ("joint2Acceleration", c_float),
        ("joint3Acceleration", c_float),
        ("joint4Acceleration", c_float)
        ]

class JOGCoordinateParams(Structure):
    _pack_ = 1
    _fields_ = [
        ("xVelocity", c_float),
        ("yVelocity", c_float),
        ("zVelocity", c_float),
        ("rVelocity", c_float),
        ("xAcceleration", c_float),
        ("yAcceleration", c_float),
        ("zAcceleration", c_float),
        ("rAcceleration", c_float)
        ]

class JOGCommonParams(Structure):
    _pack_ = 1
    _fields_ = [
        ("velocityRatio", c_float),
        ("accelerationRatio", c_float)
        ]

class JOGLParams(Structure):
    _pack_ = 1
    _fields_ = [
        ("velocity",  c_float),
        ("acceleration",  c_float)
    ]


JC = enum(JogIdle=0,
    JogAPPressed=1,
    JogANPressed=2,
    JogBPPressed=3,
    JogBNPressed=4,
    JogCPPressed=5,
    JogCNPressed=6,
    JogDPPressed=7,
    JogDNPressed=8,
    JogEPPressed=9,
    JogENPressed=10)

class JOGCmd(Structure):
    _pack_ = 1
    _fields_ = [
        ("isJoint", c_byte),
        ("cmd", c_byte)
        ]

##################  再现运动部分   ##################

class PTPJointParams(Structure):
    _fields_ = [
        ("joint1Velocity", c_float),
        ("joint2Velocity", c_float),
        ("joint3Velocity", c_float),
        ("joint4Velocity", c_float),
        ("joint1Acceleration", c_float),
        ("joint2Acceleration", c_float),
        ("joint3Acceleration", c_float),
        ("joint4Acceleration", c_float)
        ]

class PTPCoordinateParams(Structure):
    _fields_ = [
        ("xyzVelocity", c_float),
        ("rVelocity", c_float),
        ("xyzAcceleration", c_float),
        ("rAcceleration", c_float)
        ]

class PTPLParams(Structure):
    _pack_ = 1
    _fields_ = [
        ("velocity",  c_float),
        ("acceleration",  c_float)
    ]

class PTPJumpParams(Structure):
    _pack_ = 1
    _fields_ = [
        ("jumpHeight", c_float),
        ("zLimit", c_float)
        ]

class PTPCommonParams(Structure):
    _pack_ = 1
    _fields_ = [
        ("velocityRatio", c_float),
        ("accelerationRatio", c_float)
        ]

PTPMode = enum(
    PTPJUMPXYZMode=0,
    PTPMOVJXYZMode=1,
    PTPMOVLXYZMode=2,

    PTPJUMPANGLEMode=3,
    PTPMOVJANGLEMode=4,
    PTPMOVLANGLEMode=5,

    PTPMOVJANGLEINCMode=6,
    PTPMOVLXYZINCMode=7,
    PTPMOVJXYZINCMode=8,

    PTPJUMPMOVLXYZMode=9)

InputPin = enum( InputPinNone=0,
    InputPin1=1,
    InputPin2=2,
    InputPin3=3,
    InputPin4=4,
    InputPin5=5,
    InputPin6=6,
    InputPin7=7,
    InputPin8=8)

InputLevel = enum(InputLevelBoth=0,
    InputLevelLow=1,
    InputLevelHigh=2)

OutputPin = enum(
    SIGNALS_O1=1,
    SIGNALS_O2=2,
    SIGNALS_O3=3,
    SIGNALS_O4=4,
    SIGNALS_O5=5,
    SIGNALS_O6=6,
    SIGNALS_O7=7,
    SIGNALS_O8=8)

class PTPCmd(Structure):
    _pack_ = 1
    _fields_ = [
        ("ptpMode", c_byte),
        ("x", c_float),
        ("y", c_float),
        ("z", c_float),
        ("rHead", c_float)
        ]

class DeviceCountInfo(Structure):
    _pack_ = 1
    _fields_ = [
        ("deviceRunTime",  c_uint64),
        ("devicePowerOn",  c_uint32),
        ("devicePowerOff", c_uint32)
        ]

class PTPWithLCmd(Structure):
    _pack_ = 1
    _fields_ = [
        ("ptpMode", c_byte),
        ("x", c_float),
        ("y", c_float),
        ("z", c_float),
        ("rHead", c_float),
        ("l", c_float)
        ]

##################  Continuous path   ##################

class CPParams(Structure):
    _pack_ = 1
    _fields_ = [
        ("planAcc", c_float),
        ("juncitionVel", c_float),
        ("acc", c_float),
        ("realTimeTrack",  c_byte)
        ]

ContinuousPathMode = enum(
    CPRelativeMode=0,
    CPAbsoluteMode=1)

class CPCmd(Structure):
    _pack_ = 1
    _fields_ = [
        ("cpMode", c_byte),
        ("x", c_float),
        ("y", c_float),
        ("z", c_float),
        ("velocity", c_float)
        ]

class CP2Cmd(Structure):
    _pack_ = 1
    _fields_ = [
        ("cpMode", c_byte),
        ("x", c_float),
        ("y", c_float),
        ("z", c_float),
        ("velocity", c_float)
        ]

class CPCommonParams(Structure):
    _pack_ = 1
    _fields_ = [
        ("velocityRatio", c_float),
        ("accelerationRatio", c_float)
        ]

##################  圆弧：ARC   ##################
class ARCPoint(Structure):
    _pack_ = 1
    _fields_ = [
        ("x", c_float),
        ("y", c_float),
        ("z", c_float),
        ("rHead", c_float)
    ]

class ARCParams(Structure):
    _pack_ = 1
    _fields_ = [
        ("xyzVelocity", c_float),
        ("rVelocity", c_float),
        ("xyzAcceleration", c_float),
        ("rAcceleration", c_float)
        ]

class ARCCmd(Structure):
    _pack_ = 1
    _fields_ = [
        ("cirPoint", ARCPoint),
        ("toPoint", ARCPoint)
    ]

class CircleCmd(Structure):
    _pack_ = 1
    _fields_ = [
        ("cirPoint", ARCPoint),
        ("toPoint", ARCPoint)
    ]

class ARCCommonParams(Structure):
    _pack_ = 1
    _fields_ = [
        ("velocityRatio", c_float),
        ("accelerationRatio", c_float)
        ]

##################  User parameters   ##################

class WAITParams(Structure):
    _pack_ = 1
    _fields_ = [
        ("unitType", c_byte)
        ]

class WAITCmd(Structure):
    _pack_ = 1
    _fields_ = [
        ("waitTime", c_uint32)
        ]

TRIGMode = enum(
    TRIGInputIOMode = 0,
    TRIGADCMode=1)

TRIGInputIOCondition = enum(
    TRIGInputIOEqual = 0,
    TRIGInputIONotEqual=1)

TRIGADCCondition = enum(
    TRIGADCLT = 0,
    TRIGADCLE=1,
    TRIGADCGE = 2,
    TRIGADCGT=3)

class TRIGCmd(Structure):
    _pack_ = 1
    _fields_ = [
        ("address", c_byte),
        ("mode", c_byte),
        ("condition",  c_byte),
        ("threshold", c_uint16)
        ]

GPIOType = enum(
    GPIOTypeDummy = 0,
    GPIOTypeDO = 1,
    GPIOTypePWM=2,
    GPIOTypeDI=3,
    GPIOTypeADC=4,
    GPIOTypeDIPU=5,
    GPIOTypeDIPD=6)

class IOMultiplexing(Structure):
    _pack_ = 1
    _fields_ = [
        ("address", c_byte),
        ("multiplex", c_byte)
        ]

class IODO(Structure):
    _pack_ = 1
    _fields_ = [
        ("address", c_byte),
        ("level", c_byte)
        ]

class IOPWM(Structure):
    _pack_ = 1
    _fields_ = [
        ("address", c_byte),
        ("frequency", c_float),
        ("dutyCycle", c_float)
        ]

class IODI(Structure):
    _pack_ = 1
    _fields_ = [
        ("address", c_byte),
        ("level", c_byte)
        ]

class IOADC(Structure):
    _pack_ = 1
    _fields_ = [
        ("address", c_byte),
        ("value", c_int)
        ]

class UserParams(Structure):
    _pack_ = 1
    _fields_ = [
        ("params1", c_float),
        ("params2", c_float),
        ("params3", c_float),
        ("params4", c_float),
        ("params5", c_float),
        ("params6", c_float),
        ("params7", c_float),
        ("params8", c_float)
        ]

ZDFCalibStatus = enum(
    ZDFCalibNotFinished=0,
    ZDFCalibFinished=1)
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

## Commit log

2020-12-02 Initial additions of starting platform
    [all_positions_print.csv, platform_log.xlsx, test_info_array.xlsx]
2020-12-09 Added continuous open of refuel or printing valve
2020-12-09 Adjustment of the calibrations
    [all_positions_print.csv]
2020-12-09 Fixed resistance calibration bugs and added pressure controller testing
2020-12-09 Added calibrations to gitignore
2020-12-16 Reversed the order of the pressure regulators
2020-12-22 Created a printer head class and automated resistance
2020-12-22 Changed tube placement to rack
2020-12-23 Added all the CAD files for 3D printing and laser cutting
    [arm-plate_holder_template.SLDPRT, balance_tube_holder.SLDPRT, balance_tube_holder.STL, gripper_adapter_print_side.SLDPRT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]
2020-12-23 Added the valve control circuit diagram
2020-12-23 Test inserting picture
2020-12-23 added droplet printing figure
2020-12-27 Added a general figure for droplet printing
2020-12-27 Added calibration equations
2020-12-28 Added image of gripper attachment
2021-04-30 Adjusted print_calibrations
2021-04-30 Added two print arrays
    [water_100wells.csv, wce_100wells.csv]
2021-05-08 Modified the calibrations for the Dobot M1 and how to access them.
2021-05-11 Modified API and arduino code to print more robustly
    [test_384wells.csv, test_384wells_10drops.csv]
2021-05-27 arduino-python communication bug fix
2021-06-02 Added first iteraction of empirical chip calibration
2021-06-02 Modified old resistance calculation function
2021-06-02 Clean up of printing function and switching of the pressure channels
2021-06-03 Added a set of print arrays to setup 96 cell-free reactions
    [CF-print_DNA_4drops.csv, CF-print_water_3drops.csv, CF-print_wce_26drops.csv]
2021-06-03 Small modifications to the chip calibration protocol
2021-06-03 Added print arrays for mCherry test
    [all_positions_print.csv, mCh test-GFP-130.0.csv, mCh test-GFP-2.03.csv, mCh test-GFP-32.5.csv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]
2021-07-01 bR-GFP11 dobot M1 test arrays
    [eCM212-bR_G M1 gradient-bR_G-247.5.csv, eCM212-bR_G M1 gradient-bR_G-49.5.csv, eCM212-bR_G M1 gradient-bR_G-8.25.csv, eCM212-bR_G M1 gradient-lipo-20.0.csv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]
2021-07-09 Cleaned up the calibration and array printing functions
2021-07-09 Added all eCM213 print arrays
    [eCM213-bR_G+lipo_fine M1 gradient---bR_G-115.5.csv, eCM213-bR_G+lipo_fine M1 gradient---bR_G-132.0.csv, eCM213-bR_G+lipo_fine M1 gradient---bR_G-33.0.csv, eCM2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]
2021-07-13 Fixed bugs in the printer head calibration function
2021-07-20 Numerous modifications to test the p1000 pipet tip adapter
    [test_1_drop_30wells.csv, test_1_drop_4wells.csv]
2021-08-13 Added the pause buttom while printing arrays
2021-08-16 Moved the getpose function to the get dobot calibration function
2021-08-17 Added pipet calibration and volume tracking for pipet printing
